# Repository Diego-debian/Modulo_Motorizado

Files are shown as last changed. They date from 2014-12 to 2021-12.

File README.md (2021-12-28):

Modulo Motorizado
=================

Bienvenido a este proyecto, el cual tiene como finalidad desarrollar un vehículo motorizado para poder ilustrar ciertas propiedades de las ondas electromagnéticas como los son: difracción, absorbción y atenuación; en este repositorio encontrara:
 1. Instalación de los paquetes de software necesarios.
 2. Los planos eléctricos del hardware.
 3. Programación del microcontrolador atmega 328
 4. Programa para la obtención de datos y graficador en tiempo real de dichos datos.
 5. Guías de elaboración de los laboratorios propuestos para ilustrar las propiedades de la radiación electromagnética. 
 6. Análisis de datos.
 7. Licencia de software.

Para comenzar la descarga del repositorio así como su instalación haga clic en la carpeta [0. Inicio] (/0. Instalación/)

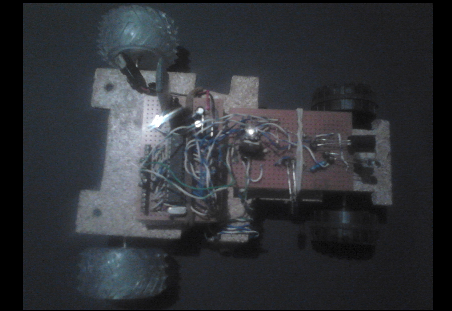
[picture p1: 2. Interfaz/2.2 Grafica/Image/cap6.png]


Objetivos
=========

# Generales 

 * Utilizar tecnologías libres para la realización de este proyecto.
 * Crear un modulo motorizado controlado vía bluetooth para ilustrar propiedades de la radiación infrarroja como lo son la difracción, la absorción y la atenuación. 

## Específicos 

 * Utilizar un Sistema operativo GNU-Linux como plataforma para el desarrollo del software que va a controlar el hardware del dispositivo.
 * Con el microcontrolador atmega328P-PU  realizar la parte de control del hardware.
 * Utilizar diodos led infrarrojos, tanto receptores como emisores, para la   construcción del sensor que llevara integrado nuestro proyecto.
 * Utilizar un motor a 9 voltios DC e integrarlo al vehículo, junto con un transistor TIP 122   para el control de la velocidad del motor.
 * Utilizar un modulo Bluetooth HC-06 para arduino, el cual permita la comunicación a distancia con el dispositivo, sin necesidad de un sistema físico cableado.
 * Utilizar un transistor LM-7805CV para construir un transformador de voltaje de 9 voltios a 5 voltios para poder alimentar el microcontrolador atmega328P-PU, y los demás dispositivos del proyecto.
 * Encontrar el patrón de difracción de los diodos emisores en infrarrojo para determinar la longitud de onda de los diodos.
 * Encontrar una constante en el patrón de absorción de diferentes materiales que nos permita clasificarlos por su capacidad de absorber radiación infrarroja.
 * Encontrar una constante en el patrón de atenuación la cual nos tiene que llevar a la conclusión de como se atenúa este tipo de radiación a través del espacio.

Metodología 
===========

 * Diseñar  una placa micro controladora que sea muy parecida a la placa arduino uno, con diodos emisores y receptores infrarrojos, resistencias, condensadores para la creación de los instrumentos de medición.
 * Construir un modulo motorizado “Vehículo motorizado”, con instrumentos para el análisis de radiación infrarroja, en donde reposara nuestra placa micro controladora y sus respectivos instrumentos de medición.
 * Utilizar un sistema operativo de software libre como lo es debian 7 Jessie o Linux mint 17, y con programas como  arduino, python, c++, octave, gnuplot, libreoffice, kile, fritzing y emacs para la creación del software.
 * Crear el software, adaptarlo y configurar bien al hardware para que no surjan errores significativos con las mediciones. 
 * Crear unas guías de laboratorio la cual sea de fácil comprensión tanto a estudiantes como profesionales que estén relacionados con estos temas.

Referencia Bibliográfica 
========================

 * Notas del curso, python para el computo científico, curso de actualización académica de la DGAPA-UNAM, Facultad de ciencias, Dr. David P. Sanders, 5 de agosto de 2013. 
 * Manual básico de uso de minicom http://www.slideshare.net/Metaconta/manual-bsico- minicom-presentation .
 * Para la placa arduino, se toma de referencia http://www.proyectosarduino.com/ 
 * Para la programación en la tarjeta micro controladora arduino se utilizara la siguiente referencia http://www.arduino.cc/es/ 
 * Para la programación en c++ y gcc, GNU/Linux, Programación de sistemas, Pablo Garaizar Sagarminaga, Facultad de Ingeniería -ESIDE, Universidad de Deusto, Bilbao. 
 * Fundamentos de circuitos eléctricos, tercera edición, editorial Mc Graw Hill, Charles K. Alexander and Matthew N. O. Sadiku. 
Manual del proyecto octave http://www.gnu.org/software/octave/doc/interpreter/ 
 * Pagina oficial del proyecto gnuplot http://www.gnuplot.info/ 
 * Pagina oficial del proyecto Libreoffice http://www.libreoffice.org/ 
 * Edición de textos científicos Latex, Walter Mora, Alexander Borbon
 * Escuela de matemática,Instituto Tecnológico de Costa Rica; Revista digital matemática, educación e Internet www.tec-digital.itcr.ac.cr/revistamatematica/ 
 * Manual del usuario emacs http://www.nongnu.org/emacs-man-es/ 
 * Pagina oficial del Sistema Operativo debian https://www.debian.org/index.es.html 
 * Pagina oficial del proyecto fritzing http://fritzing.org/home/ 
 * Física Macarenha Herrera Aguayo, Edición especial para el ministerio de educación Chileno, editorial Santillana. 
 * Berkeley Physics Course Vol 3 Ondas (Crawford), editorial Reverte 
 * Para el integrado microcontrolador atmega328 se utilizara esta pagina  http://www.futurlec.com/Atmel/ATMEGA328P-PU.shtml
 * Para el uso del TIP 122 se toma de referencia esta pagina http://pdf.datasheetcatalog.com/datasheet/fairchild/TIP122.pdf
 * Para el modulo Bluetooth HC-06 arduino se toma esta referencia http://42bots.com/tutorials/hc-06-bluetooth-module-datasheet-and-configuration-with-arduino/
 * Con el transistor LM7805CV se toma de referencia http://www.fairchildsemi.com/ds/LM/LM7805.pdf
 * Pagina oficial de Scilab http://www.scilab.org/
 * Pagina oficial de los productos  Phywe http://www.phywe.com/448/Product-Catalogue.htm

Mesa de Miembros del Proyecto
=============================

 1. Diego Alberto Parra Garzón <diegoestudianteud1@gmail.com> Desarrollador de Contenidos

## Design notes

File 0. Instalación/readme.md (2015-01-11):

Instalación 
===========

Para el correcto funcionamiento del programa es necesario instalar los siguientes programas:
 0. git 
 1. bluez* 
 2. gcc
 3. g++
 4. emacs
 5. gnuplot gnuplot-qt
 6. evince 
 7. octave
 8. python-matplotlib 
 9. python-numpy
 10. python-tk 
 11. python-gnuplot
 12. python-serial
 13. python-visual*
 14. libgtkglextmm*
 15. kile
 16. arduino 
 17. fritzing 
 18. eog
 19. arduino

Si desea o es usuario de un S.O. no mantenido por el script para su auto instalación o si solo desea instalar por su propia cuenta los programas por favor instalelos manualmente y pase a la etapa de clonar el sitio.

lo primero sera instalar git en su S.O. dependiendo su S.O. el comando puede variar en mi caso uso debian y por lo general se instala de la siguiente manera.
    
Ingresar como usuario root

    $ su  

Introducir el Password, atención por que cuando escribimos el pass no se escribe en la terinal y esto es debido a razones de seguridad, pero claro que si se esta escribiendo. Luego de logeados escribimos:

    $ apt-get install git 

Luego de instalado debera escribir en una terminal el siguiente comando, esta vez no como superusuario sino como usuario normal para esto escribimos exit, luego oprimimos enter y luego escribimos lo siguiente.

    $ git clone https://github.com/Diego-debian/Modulo_Motorizado.git

Despues de clonar el sitio nos dirijimos desde la terminal hasta donde descargamos el modulo git e ingresamos a la carpeta "Modulo_Motorizado/tree/master/0. Instalación/0.1 programas requeridos "

por favor ingrese a la carpeta antes mensionada y siga las instrucciones.

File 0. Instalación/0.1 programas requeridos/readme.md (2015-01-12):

# INSTALACION AUTOMATIZADA

Se encuentra en la parte de la instalación, en esta parte se procederá a instalar los paquetes necesarios para que el programa funcione, pues estos son requisitos fundamentales para el óptimo funcionamiento de todo el software.

 * Lo primero sera abrir una terminal y logearnos como usuario root.
 * Luego en la consola buscamos la ruta a nuestra a nuestro archivo de instalación en python la cual es "Modulo_Motorizado/tree/master/0. Instalación/0.1 programas requeridos". 
 * Encontramos un archivo llamado install.py, lo que debemos hacer es escribir en la terminal el siguiente comando.

     $ python install.py

 * El programa se ejecutara automaticamente, tendremos que esperar unos segundos mientras se carga.
 * Nos aparecera una ventana como la siguiente: 

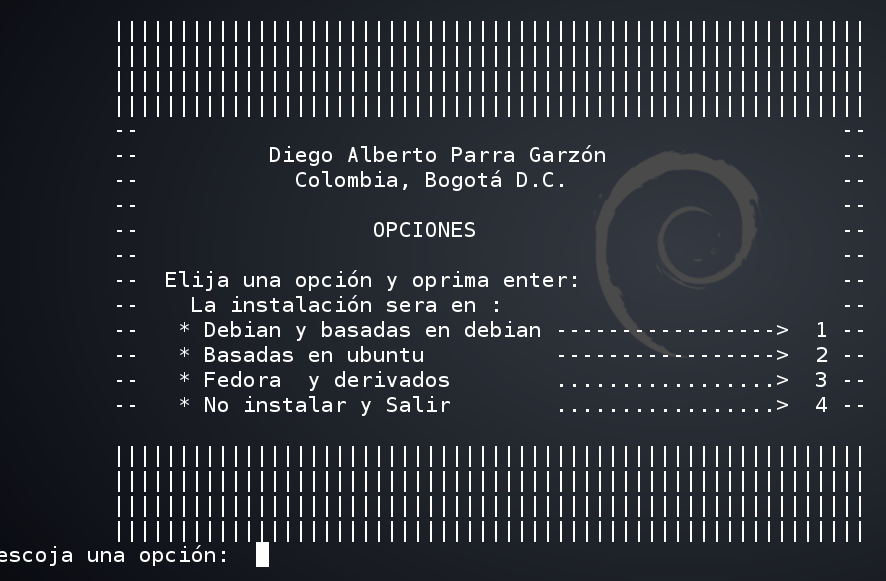
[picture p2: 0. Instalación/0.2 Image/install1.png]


 * Escogemos el S.O. que estamos usando, como ya dije de no aparecer el S.O., no hay ningún problema solo debemos instalar los paquetes antes mensionados manualmente y luego clonar el repositorio,
 * De aca en adelante le daremos "Si" a todo, y al finalizar nos aparecera la ventana de la IDE de arduino. 

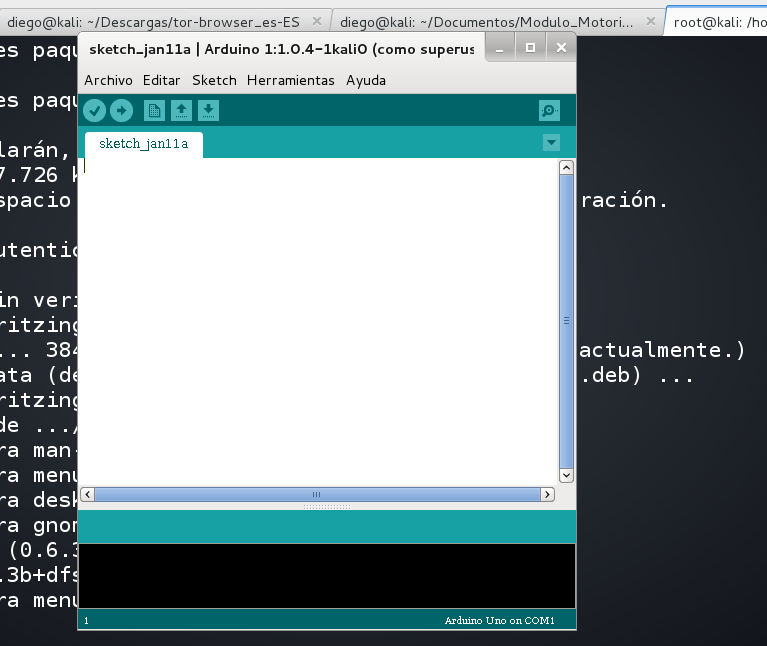
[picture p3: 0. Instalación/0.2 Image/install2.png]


 * Si se ha abierto esta ventana vamos por buen camino, ahora cerramos la ventana y el programa nos preguntara si queremos reiniciar el pc; a lo que responderemos que si.

Listo a disfrutar

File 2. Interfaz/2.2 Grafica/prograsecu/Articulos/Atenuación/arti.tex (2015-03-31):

\documentclass[12]{article}
\usepackage[spanish,english]{babel}
%\usepackage[spanish]{babel}
\usepackage[utf8]{inputenc}
\usepackage{graphicx}
\usepackage{epsfig}
\usepackage{multicol,caption}
\usepackage{amsthm} % Theorem Formatting
\usepackage{amssymb}    % Math symbols such as \mathbb
\usepackage{color}
\usepackage{hyperref}
\usepackage[none]{hyphenat}
%\renewcommand{\tablename}{Tabla}
%\def\tablename{Cuadro}% por \def\tablename{Tabla}% 
\newenvironment{Figure}
{\par\medskip\noindent\minipage{\linewidth}}
{\endminipage\par\medskip}
\addto\captionsspanish{%
\def\tablename{Tabla}%
}
\topmargin  = 10pt
\oddsidemargin  = -0.5in
%\headheight = 12pt
%\headsep    = 15pt
%\footskip   = 15pt
\textheight = 21.5 cm
\textwidth  = 18.5cm
\tolerance=10000
\title{\bf{Ilustración de la propiedad de atenuación en ondas electromagnéticas en el espectro infrarrojo, utilizando tecnologías libres y de bajo costo}}
\author{Diego Alberto Parra Garzón \footnote{diegoestudianteud1@gmail.com} \\ Universidad Distrital, Calle 3 No 26A-40 Bogotá-Colombia \\    Proyecto Curricular de Licenciatura en Física }
\date{\today}
\begin{document}
%\def\tablename{Cuadro}% por \def \tablename{Tabla}% 
\renewcommand{\tablename}{Tabla}
\maketitle
\vspace{-0.8cm}
\begin{abstract}
This article presents a new way of illustrating the attenuation property with electromagnetic waves; as the wavelengths in the infrared are also part of the electromagnetic spectrum and everyday use we give to this radiation is very wide, so it is essential to place this resource for both students and professionals, for the experimental part is combined with the theoretical giving a feedback issue. Data were obtained from a motor module equipped with an infrared sensor receiver and an infrared LED emitter, which are controlled by a atmega microcontroller 328-Pu and this is linked via Bluetooth to a computer, this process is done by the computer with the help of free software like python, gnuplot, octave among other languages, it is worth noting that everything is done in a free operating system like linux mint or debian. Data analysis laboratory, which will have to shed the value of attenuation of electromagnetic waves and has to match what is in the scientific literature will.\\ \\
{\bf{Keywords:}} Maxwell's laws, electromagnetic attenuation data nonlinear regression.
\end{abstract}
\selectlanguage{spanish}
\begin{abstract}
El presente articulo presenta una nueva forma de ilustrar la propiedad de atenuación que tienen las ondas electromagnéticas; como las longitudes de onda en el  infrarrojo también hacen parte del espectro electromagnético y el uso diario que le damos a esta radiación es muy amplio, por ello es indispensable colocar este recurso tanto para estudiantes como profesionales, pues se combina la parte experimental con lo teórico dando una retroalimentación del tema en cuestión. Se obtendrán los datos a partir de un modulo motorizado equipado con un sensor infrarrojo receptor y un led infrarrojo emisor, los cuales son controlados por un microcontrolador atmega 328-Pu y este va enlazado vía bluetooth a un ordenador, todo este proceso lo realiza el ordenador con la ayuda de software libre como python, gnuplot, octave entre otros lenguajes, cabe resaltar que todo se realiza en un sistema operativo libre como lo es linux mint o debian. Se hará el análisis de datos del laboratorio, el cual tendrá que arrojar el valor de atenuación de las ondas electromagnéticas y tiene que coincidir con el que se encuentra en la literatura científica.\\ \\
{\bf{Descriptores:}} Leyes de Maxwell, atenuación electromagnética, regresión no lineal de datos.
\end{abstract}
\begin{multicols}{2}
\section{Introducción}
El arreglo experimental esta esquematizado en la Fig. 1 y constaba de un horno con un pequeño orificio de salida para calentar el gas, luego de la salida un colimador y un selector de velocidades, y finalmente, un detector de partículas.
\end{multicols}
\end{document}

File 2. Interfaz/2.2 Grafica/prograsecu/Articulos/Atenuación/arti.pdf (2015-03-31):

# Ilustraci´on de la propiedad de atenuaci´on en ondas electromagn´eticas en el espectro infrarrojo, utilizando tecnolog´ıas libres y de bajo costo

## Diego Alberto Parra Garz´on ∗ Universidad Distrital, Calle 3 No 26A-40 Bogot´a-Colombia Proyecto Curricular de Licenciatura en F´ısica

## March 30, 2015

Abstract

This article presents a new way of illustrating the attenuation property with electromagnetic waves; as the wavelengths in the infrared are also part of the electromagnetic spectrum and everyday use we give to this radiation is very wide, so it is essential to place this resource for both students and professionals, for the experimental part is combined with the theoretical giving a feedback issue. Data were obtained from a motor module equipped with an infrared sensor receiver and an infrared LED emitter, which are controlled by a atmega microcontroller 328-Pu and this is linked via Bluetooth to a computer, this process is done by the computer with the help of free software like python, gnuplot, octave among other languages, it is worth noting that everything is done in a free operating system like linux mint or debian. Data analysis laboratory, which will have to shed the value of attenuation of electromagnetic waves and has to match what is in the scientific literature will.

Keywords: Maxwell’s laws, electromagnetic attenuation data nonlinear regression.

Abstract

El presente articulo presenta una nueva forma de ilustrar la propiedad de atenuaci´on que tienen las ondas electromagn´eticas; como las longitudes de onda en el infrarrojo tambi´en hacen parte del espectro electromagn´etico y el uso diario que le damos a esta radiaci´on es muy amplio, por ello es indispensable colocar este recurso tanto para estudiantes como profesionales, pues se combina la parte experimental con lo te´orico dando una retroalimentaci´on del tema en cuesti´on. Se obtendr´an los datos a partir de un modulo motorizado equipado con un sensor infrarrojo receptor y un led infrarrojo emisor, los cuales son controlados por un microcontrolador atmega 328-Pu y este va enlazado v´ıa bluetooth a un ordenador, todo este proceso lo realiza el ordenador con la ayuda de software libre como python, gnuplot, octave entre otros lenguajes, cabe resaltar que todo se realiza en un sistema operativo libre como lo es linux mint o debian. Se har´a el an´alisis de datos del laboratorio, el cual tendr´a que arrojar el valor de atenuaci´on de las ondas electromagn´eticas y tiene que coincidir con el que se encuentra en la literatura cient´ıfica.

Descriptores: Leyes de Maxwell, atenuaci´on electromagn´etica, regresi´on no lineal de datos.

## 1 Introducci´on

El arreglo experimental esta esquematizado en la Fig. 1 y constaba de un horno con un peque˜no orificio de salida para calentar el gas, luego de la salida un colimador y un selector de velocidades, y finalmente, un detector de part´ıculas.

∗diegoestudianteud1@gmail.com

1

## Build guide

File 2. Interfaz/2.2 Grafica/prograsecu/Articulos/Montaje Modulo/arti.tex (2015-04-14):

\documentclass[12]{article}
\usepackage[spanish,english]{babel}
%\usepackage[spanish]{babel}
\usepackage[utf8]{inputenc}
\usepackage{graphicx}
\usepackage{epsfig}
\usepackage{multirow}
\usepackage{multicol,caption}
\usepackage{amsthm} % Theorem Formatting
\usepackage{amssymb}    % Math symbols such as \mathbb
\usepackage{color}
\usepackage{hyperref}
\usepackage[none]{hyphenat}
%\renewcommand{\tablename}{Tabla}
%\def\tablename{Cuadro}% por \def\tablename{Tabla}% 
\newenvironment{Figure}
{\par\medskip\noindent\minipage{\linewidth}}
{\endminipage\par\medskip}
\addto\captionsspanish{%
\def\tablename{Tabla}%
}
\topmargin  = 10pt
\oddsidemargin  = -0.5in
%\headheight = 12pt
%\headsep    = 15pt
%\footskip   = 15pt
\textheight = 21.5 cm
\textwidth  = 18.5cm
\tolerance=10000
\title{\bf{Montaje de un modulo motorizado, con sensores infrarrojos, controlado con una tarjeta atmega 328P-PU y comunicación serial vía bluetooth en un ordenador con GNU-Linux.}}
\author{Diego Alberto Parra Garzón \footnote{diegoestudianteud1@gmail.com} \\ Universidad Distrital, Calle 3 No 26A-40 Bogotá-Colombia \\    Proyecto Curricular de Licenciatura en Física }
\date{\today}
\begin{document}
%\def\tablename{Cuadro}% por \def \tablename{Tabla}% 
\renewcommand{\tablename}{Tabla}
\maketitle
\vspace{-0.8cm}
\selectlanguage{english}

\begin{abstract}
It is necessary to visualize the extent that free technologies have today about the company, these technologies are the foundation of the economy of many countries, and why not say that it has reached an age where information and means to transmit they are available to anyone, such is the case we can take this technology and make it new tools to support the work of science teaching and learning in science, for this reason it has decided to take this whole world of free technologies, combine them and make it these new tools we need to continue this work of learning and teaching that never ends.\\ \\
illustrating the attenuation property with electromagnetic waves; as the wavelengths in the infrared are also part of the electromagnetic spectrum and everyday use we give to this radiation is very wide, so it is essential to place this resource for both students and professionals, for the experimental part is combined with the theoretical giving a feedback issue. Data were obtained from a motor module equipped with an infrared sensor receiver and an infrared LED emitter, which are controlled by a atmega microcontroller 328-Pu and this is linked via Bluetooth to a computer, this process is done by the computer with the help of free software like python, gnuplot, octave among other languages, it is worth noting that everything is done in a free operating system like linux mint or debian. Data analysis laboratory, which will have to shed the value of attenuation of electromagnetic waves and has to mat.\\ 
{\bf{Keywords:}} Motor module, infrared sensors, microcontroller module bluetooth, electromagnetic wave.

\selectlanguage{spanish}
\begin{center}
{\bf{Resumen}} 
\end{center}

Es necesario visualizar el alcance que las tecnologías libres tienen el día de hoy sobre la sociedad, estas tecnologías son las bases de las economías de muchos países, y porque no decirlo que se ha alcanzado una era en donde la información y los medios que la transmiten están al alcance de cualquier persona,  tal es el caso que podemos tomar esta tecnología y hacer de ella nuevos instrumentos que respalden la labor de la enseñanza científica y el aprendizaje en ciencias, por esta razón se ha decidido tomar todo este mundo de tecnologías libres, combinarlas y hacer de ella esos nuevos instrumentos que necesitamos para continuar con esta labor de aprendizaje y enseñanza que no termina nunca.\\\\
Este articulo espera ser acogido por estudiantes y profesionales que vean en este un modelo didáctico,  con materiales que consiguen fácilmente y con un gran poder de exactitud en las mediciones; en este  se ilustra un montaje experimental, de un modulo motorizado o en otras palabras un dispositivo móvil impulsado por un motor en este caso eléctrico; está equipado con un microcontrolador atmega 328P-PU, este se encargara de toda la parte de control de los demás elementos eléctricos, dispondrá de dos diodos led receptores en el infrarrojo   de GaAs, también consta de un diodo led emisor en el infrarrojo de GaAs, un modulo bluetooth hc-06 para arduino y una batería de 9 voltios junto con un regulador de 9V a 5V.  Todo esto con el fin de poder hacer mediciones de la intensidad de la radiación producida por estos diodos y calibrar el dispositivo para aplicaciones ilustrativas de las propiedades de las ondas electromagnéticas y su dualidad onda – partícula. \\
{\bf{Descriptores:}} Modulo motorizado, sensores infrarrojos, microcontrolador, modulo bluetooth, ondas electromagnéticas. 
\end{abstract}

\begin{multicols}{2}
\section{Introducción}
Al no poderse descartar la realidad de las tecnologías libres, su rápido crecimiento y el hecho de que sean muy sencillas de utilizar, ha sido el detonante para la realización de este proyecto; el cual pretende elaborar un sistema electrónico-mecánico que sea controlado vía bluetooth, sin necesidad de un sistema físico de cables; este debe tener la cualidad de ser lo más exacto posible en cuanto a la captura y manipulación de datos; sin dejar a un lado su bajo costo. \\\\ También tiene la pretensión de ser un modelo didáctico, que pueda ser utilizado en la enseñanza de la ciencia de una manera practica, llamativa, con la cual el estudiante pueda tener una sensación de que las ciencias son divertidas, sin dejar de lado su exactitud y su carácter de buscar el ¿por qué?,  los ¿cómo?, y la precisión al compararse la teoría con la parte experimental.

\section{Configuración experimental}

{\bf{2.1 Materiales para el montaje}} \\

Para la realización de este montaje se utilizaron los siguientes materiales:
\begin{enumerate}
\item[a.] Un ordenador con un sistema operativo GNU-Linux.
\item[b.] Microcontrolador atmega 328P-PU \cite{ARDUINO} para realizar la parte de control del hardware.
\item[c.] Dos diodos led infrarrojos\cite{INFRARED} receptores.
\item[d.] Un diodo led infrarrojo\cite{INFRARED} emisor.
\item[e.] Un motor a 9 voltios DC, junto con un transistor TIP 122\cite{TIP122}   para el control de la velocidad de giro del engranaje del motor.
\item[f.] Modulo Bluetooth HC-06 para arduino, el cual permita la comunicación a distancia con el dispositivo, sin necesidad de un sistema físico cableado.
\item[g.] Transistor LM-7805CV \cite{REGULADOR} para un transformador de voltaje de 9 voltios a 5 voltios el cual alimentara el microcontrolador atmega328P-PU, y los demás dispositivos del proyecto.
\item[h.] Un cristal de 16 MHz.
\item[i.] Tarjeta arduino \cite{ARDUINO} uno.
\item[j.] Tres resistencias de 220 ohms a 500 ohms.
\item[h.] Dos resistencia de 500 ohms.
\item[i.] Tres resistencias de 1 komhs.
\item[j.] Diodo rectificador de referencia 1N4001. \cite{DIODO}
\item[k.] Dos capacitores cerámicos de 12 picofaradios.
\item[l.] Dos capacitores de 10 microfaradios.
\item[m.] Sistema de engranajes de eje móvil, para realizar el movimiento del vehículo.
\item[n.] Cuatro llantas de carros de juguetes.
\item[ñ.] Una batería de 9 V.
\item[o.] Una tabla o un acrílico de 14x12x0.3 $cm^{3}$
\item[p.] Un interruptor pequeño.
\end{enumerate}

{\bf{2.2 Montaje experimental}}\\\\
{\bf{2.2.1 Circuito electrónico}}\\\\
A continuación se explica paso a paso como armar el circuito eléctrico, el montaje se realiza en fritzing\footnote{Enlace a la pagina oficial del proyecto fritzing http://www.fritzing.org/home/}. Se explicara parte por parte del circuito y luego todas deben unirse en una sola.\\\\
Cabe mencionar que los esquemas de las figuras de la 1 a la 8 fueron tomadas de la pagina principal del proyecto arduino\cite{ARDUINO}, y modificadas en fritzing\cite{FRITZING}  \\\\
Lo primero que se hará, sera preparar el microcontrolador para su primer uso, debido a que los microcontroladores atmega 328 P-PU no vienen listos para comenzar a programar; es necesario hacer un stand alone\footnote{Enlace a un bootloader https://arduinoelectronics.wordpress.com/2012/02/10/standalone-atmega-without-arduino-bootloader/} sobre el microcontrolador.\\\\

\begin{Figure}
\center
\begin{tabular}{|l|r|}
\hline
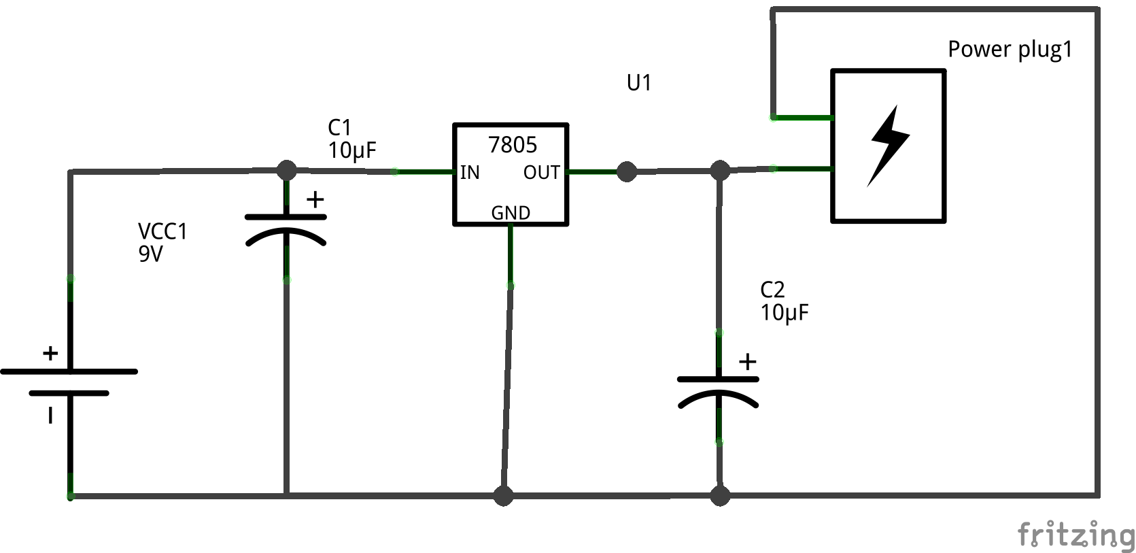
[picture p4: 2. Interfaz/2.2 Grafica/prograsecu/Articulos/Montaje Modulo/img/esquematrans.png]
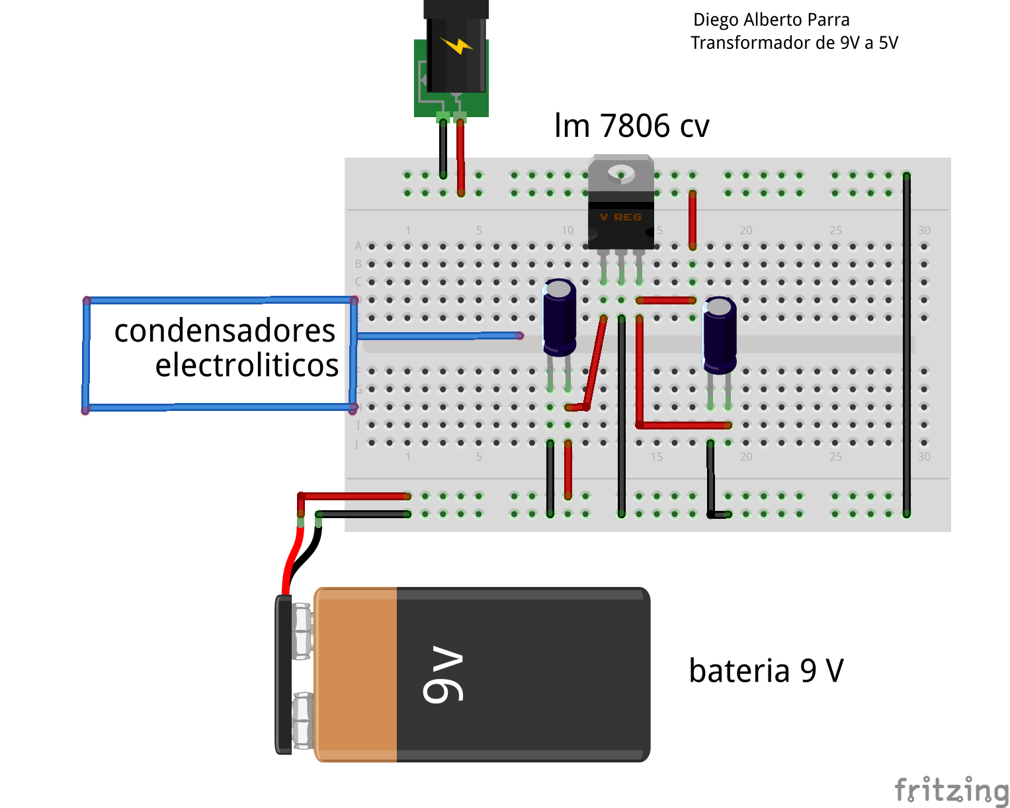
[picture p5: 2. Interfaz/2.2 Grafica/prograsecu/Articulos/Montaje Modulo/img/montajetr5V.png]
  &  \\ \hline
1.A. & 1.B \\ \hline
\end{tabular}
\captionof{figure}{En la figura 1.A. se observa el esquema eléctrico de un transformador \cite{REGULADOR} de 9V a 5V, utilizando un transistor lm 7805 cv. Los capacitores son electrolíticos de 10 microfaradios.  En la figura 1.B. se observa el montaje en protoboard del circuito regulador.}
\label{fig:g1}
\end{Figure}
\vspace{0.2cm}

Montamos un transformador de 9 voltios a 5 voltios, esto lo hacemos con dos capacitores electrolíticos de 10 microfaradios  y el transistor lm7805\cite{REGULADOR} cv. Ambos  capacitores deben ir en paralelo quedando su extremo negativo conectado a tierra y su extremo positivo uno a la entrada de 9 V y el otro a la salida de 5 V del transistor, el transistor lm consta de 3 pines uno de los cuales es la entrada de +9V, el pin de la mitad es tierra o GND y el pin extremo es la salida a 5V; tal como se muestra en la figura 1.A.; en la figura 1.B. se le coloco un enchufe de salida de poder.
El modulo bluetooth se debe conectar de la siguiente manera: el pin 2 de la tarjeta arduino es el Rx este va conectado al Tx del blueetooth, el pin 3 del microcontrolador es el Tx y va conectado al pin Rx del bluetooth, como se muestra en la figura 2.A y 2.B , conectamos el GND del bluetooth al pin 8  o 16 de nuestro microcontrolador , ahora conectamos el pin de Vcc del bluetooth al pin 7 o 14 del microcontrolador. \\\\
Necesitamos colocar un oscilador de 16 mHz el cual lo dejaremos siempre en el microcontrolador, esto  con el fin de ajustar los tres relojes internos que trae nuestro integrado atmega 328 P-Pu, para esto utilizamos el cristal de 16 mHz junto con los dos condensadores cerámicos de 12 picofaradios \footnote{Ver figura 2.A y 2.B.}, uno de los pines del cristal debe conectarse al pin 9 del microcontrolador y el otro extremo del cristal al pin 10, conectamos un capacitor a cada extremo del cristal y estos al pin 8 o 16 del microcontrolador de tal forma que los capacitores quedan en paralelo. \\\\
Colocamos un botón\footnote{Como se muestra en la figura 2.A y 2.B.} para reiniciar nuestro microcontrolador en caso de que lo necesitamos, esto lo hacemos colocando uno de los extremos del botón al pin 1 del microcontrolador que es el pin de reset, el otro extremo del botón lo conectamos a una resistencia de 1 Komhs y el extremo de la resistencia a tierra.\\\\

\begin{Figure}
\center
\begin{tabular}{|l|r|}
\hline
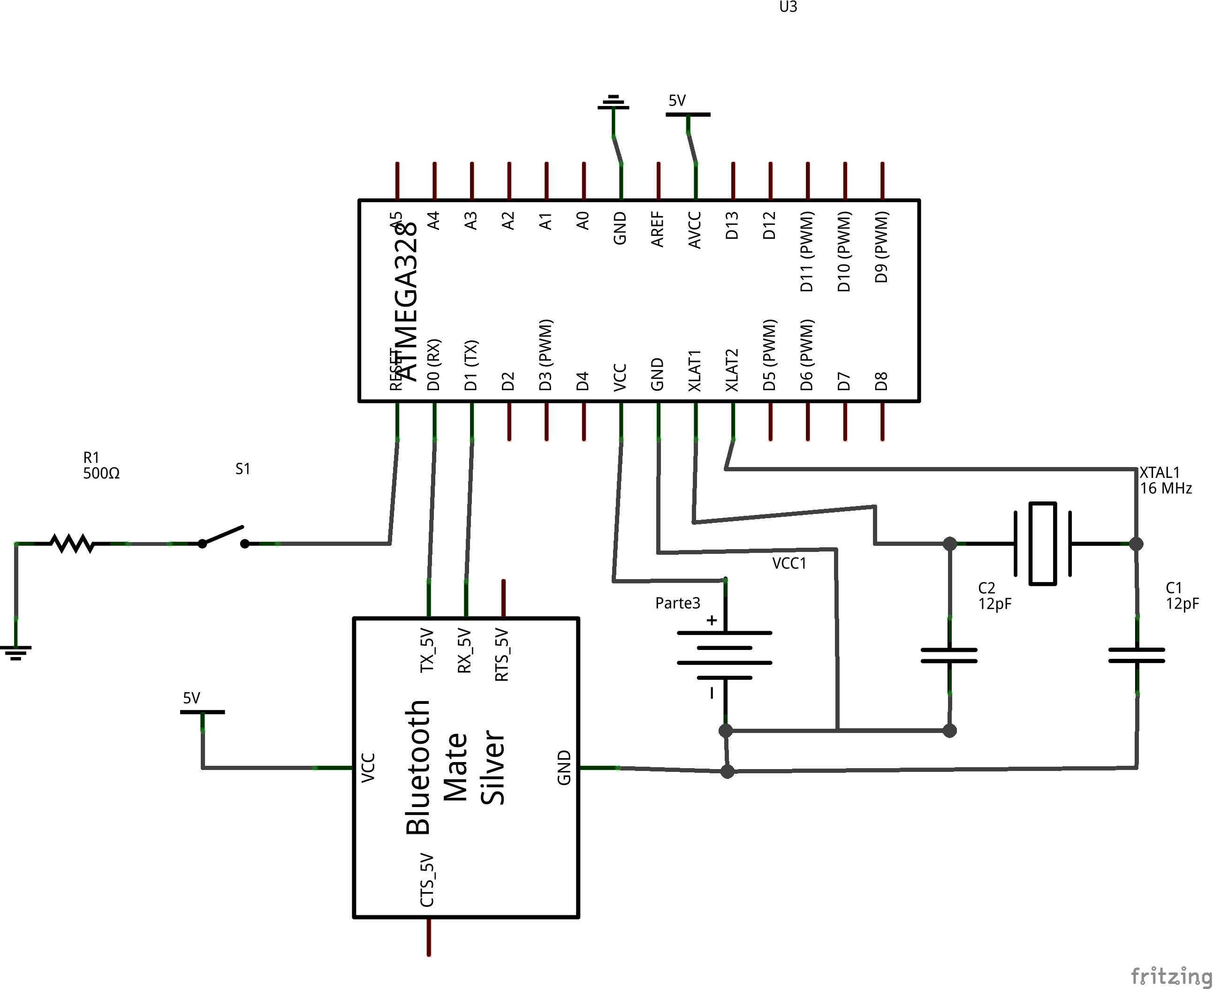
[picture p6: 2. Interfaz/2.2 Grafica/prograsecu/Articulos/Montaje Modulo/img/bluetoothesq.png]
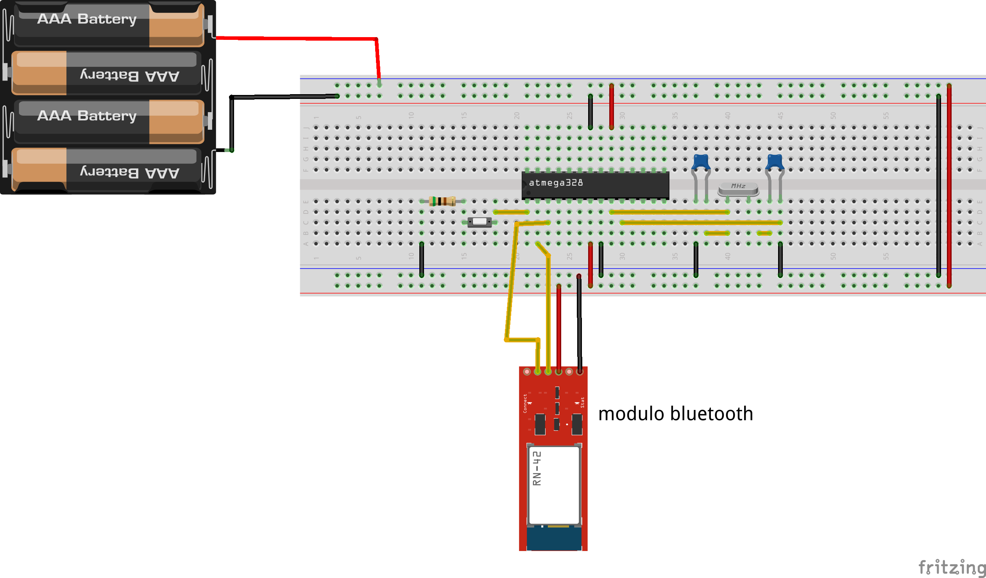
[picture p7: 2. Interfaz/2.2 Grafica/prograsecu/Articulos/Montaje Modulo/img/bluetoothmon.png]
 &  \\ \hline
2.A. & 2.B. \\ \hline
\end{tabular}
\captionof{figure}{En la figura 2.A se muestra el circuito eléctrico de un bluetooth conectado a un microcontrolador atmega 328 P-PU junto con un cristal, dos capacitores cerámicos, un botón de reset y una resistencia de 1 Komhs. En la figura 2.B esta  el montaje en protoboard, los cables negros son tierra, los cables rojos son voltaje, y los cables amarillos son conexiones.}
\label{fig:g2}
\end{Figure}
\vspace{0.2cm}

Las conexiones del motor son las siguientes, como vamos a utilizar un transistor tip\cite{TIP122} 122, los pines mostrados en la figura 2.B.  están de la siguiente manera: 

\begin{enumerate}
\item[*] El pin del lado izquierdo del transistor es la base.
\item[*] El pin del centro es el colector.
\item[*] El pin de la derecha es el emisor.
\end{enumerate}

Conectamos una resistencia de 1 $k \Omega $ al pin base del transistor y este a su vez al pin numero 5 del integrado atmega328P-PU\footnote{Como se aprecia en la figura 2.B.}, luego conectamos el pin del colector del tip122 a +5V, asegurándonos de colocar el diodo regulador entre el colector y uno de los extremos del motor; a continuación conectamos el pin emisor del transistor  junto con el otro extremo de la conexión del motor a tierra; ahora colocamos las conexiones del condensador cerámico entre las conexiones del motor.\footnote{Observar figuras 2.A. y 2.B.}

\begin{Figure}
\center
\begin{tabular}{|l|r|}
\hline
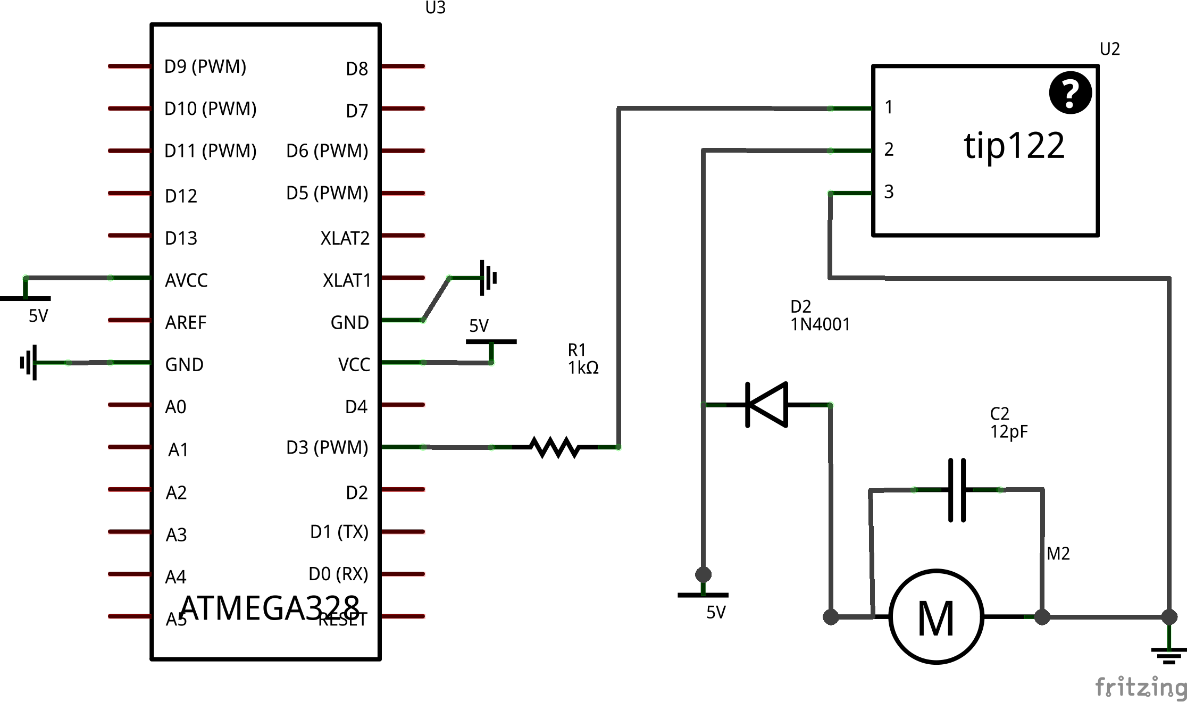
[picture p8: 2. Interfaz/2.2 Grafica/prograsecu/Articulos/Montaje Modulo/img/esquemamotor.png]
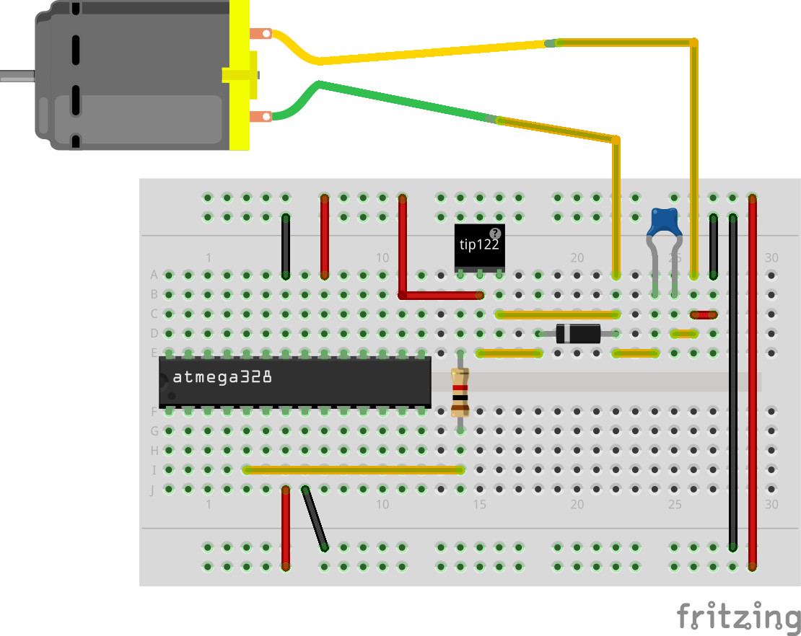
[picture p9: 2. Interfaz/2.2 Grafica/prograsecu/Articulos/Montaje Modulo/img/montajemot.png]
 &  \\ \hline
3.A. & 3.B. \\ \hline
\end{tabular}
\captionof{figure}{En la figura 3.A se muestra el circuito eléctrico del motor conectado a la tarjeta atmega 328 P-PU, junto con un tip 122 encargado de controlar la corriente que circula por el  motor consiguiendo de esta manera controlar la velocidad de este, también lleva un diodo regulador, un capacitor cerámico de  12 picofaradios y una resistencia de 1 Komhs. En la figura 3.B esta  el montaje en protoboard, los cables negros son tierra, los cables rojos son voltaje, y los cables naranjas son conexiones.}
\label{fig:g3}
\end{Figure}

Procedemos hacer las conexiones del sensor receptor lateral \footnote{Se aprecia en la figura 4.A. y en la figura 4.B.} el cual es un diodo led receptor de luz infrarroja \cite{INFRARED}, conectamos una resistencia de $1 k\Omega$ al ánodo del led y el otro extremo de la resistencia a tierra, luego conectamos el pin 28 \footnote{Este pin es la entrada analógica numero cero del microcontrolador atmega.} del microcontrolador en un punto intermedio entre la resistencia y el ánodo del diodo led, el cátodo del diodo lo conectamos a +5V.\\\\
Para las conexiones del sensor receptor frontal \footnote{Se aprecia en la figura 4.A. y en la figura 4.B., en la parte donde están los dos diodos led.} el cual es un diodo led receptor de luz infrarroja \cite{INFRARED}, conectamos una resistencia de $1 k\Omega$ al ánodo del led y el otro extremo de la resistencia a tierra, luego conectamos el pin 22 \footnote{Este pin es la entrada analógica numero cinco del microcontrolador atmega.} del microcontrolador en un punto intermedio entre la resistencia y el ánodo del diodo led, el cátodo del diodo lo conectamos a +5V.\\\\
Para la conexión de la fuente\footnote{Ver figura 4.B. y su esquema en la figura 4.A.} emisora de fotones infrarrojos o radiación infrarroja se utiliza un diodo led emisor en el infrarrojo, el cátodo del diodo lo conectamos a una resistencia de $350 \Omega$ a $500 \Omega$ y el otro extremo de la resistencia lo conectamos a tierra, el ánodo del diodo lo conectamos al pin 12\footnote{Salida D6 PWM.} del microcontrolador.

\begin{Figure}
\center
\begin{tabular}{|l|r|}
\hline
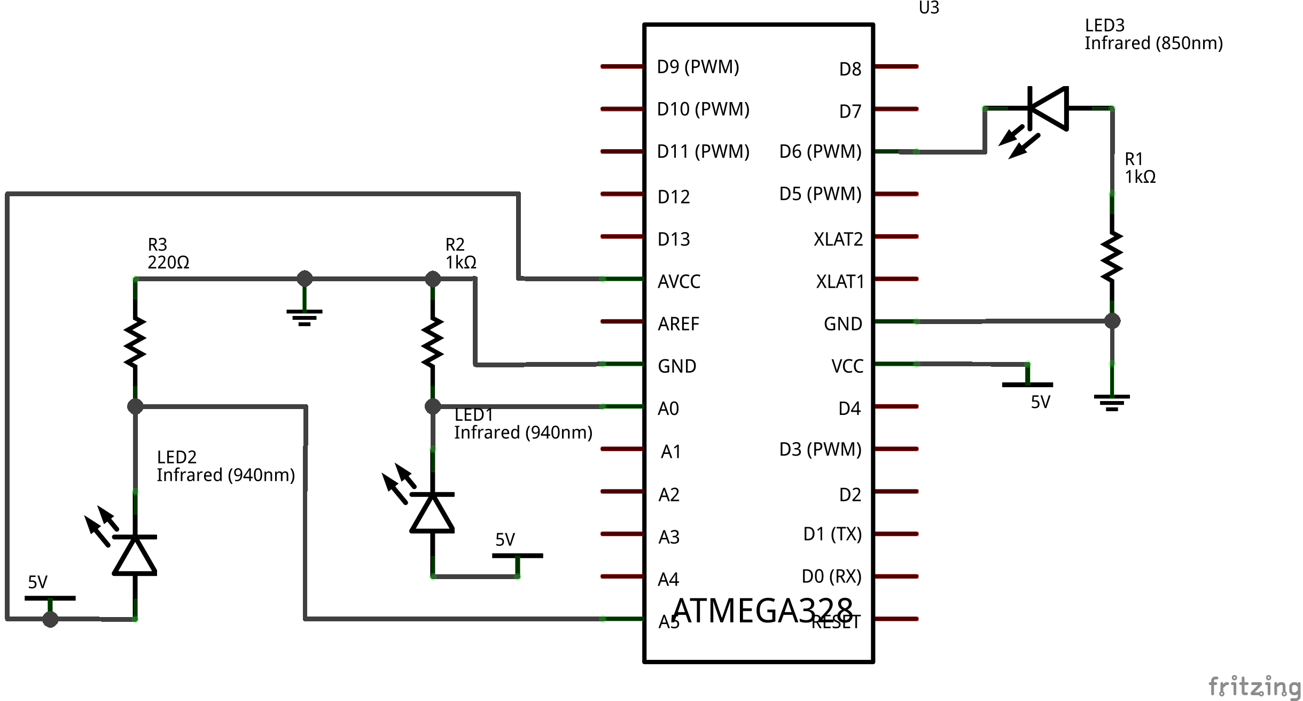
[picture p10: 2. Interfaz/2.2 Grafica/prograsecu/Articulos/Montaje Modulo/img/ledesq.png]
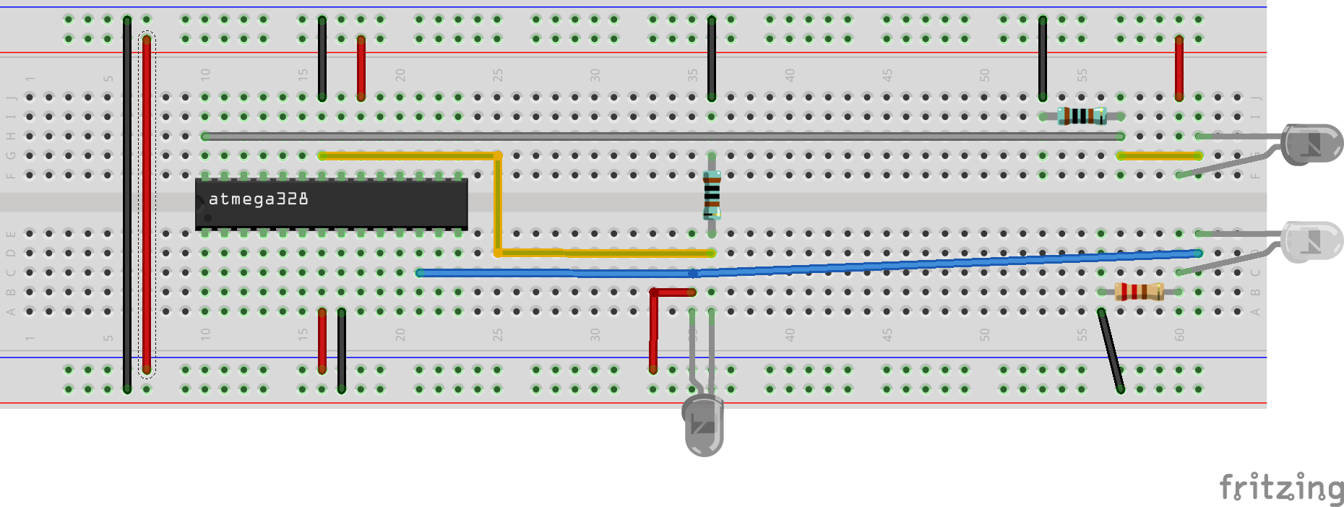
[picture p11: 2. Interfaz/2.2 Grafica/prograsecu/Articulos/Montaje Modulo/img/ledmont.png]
 &  \\ \hline
4.A. & 4.B. \\ \hline
\end{tabular}
\captionof{figure}{En la figura 4.A se observa las conexiones de los diodos tanto receptores como el emisor, conectamos al microcontrolador atmega328P-PU. En la figura 4.B esta  el montaje en protoboard, los cables negros son tierra, los cables rojos son voltaje, el cable azul es la conexión entre el ánodo del diodo led emisor infrarrojo frontal y el pin 6 del microcontrolador, el cable naranja es la conexión entre el pin 23 del microcontrolador y el punto de conexión entre el ánodo del  diodo receptor infrarrojo lateral con la resistencia, el cable gris  es la conexión entre el pin 28 del microcontrolador y el punto de conexión entre el ánodo del diodo receptor infrarrojo frontal con la resistencia.}
\label{fig:g4}
\end{Figure}

Las conexiones\footnote{Ver los esquemas de la figura 5.A. y 5.B.} del diodo rgb de ánodo común es la siguiente: conectamos el ánodo del diodo rgb a +5V, el pin rojo del diodo rgb lo conectamos a una resistencia de $500\Omega$ y el otro extremo de la resistencia conectado al pin 18 del microcontrolador, el pin verde del diodo rgb lo conectamos a una resistencia de $500\Omega$ y el otro extremo de la resistencia conectado al pin 16 del microcontrolador, el pin azul del diodo rgb lo conectamos a una resistencia de $500\Omega$ y el otro extremo de la resistencia conectado al pin 15 del microcontrolador.\\\\
Una vez terminadas las conexiones solo resta soldarlas en una baquela. Por ultimo pero no menos importante es conseguir icopor y hacer unas bases para que en ellas repose nuestro circuito de esta manera nos aseguramos en caso de cualquier incidente que las placas no se vayan a estropear ni que las conexiones vayan a quedar haciendo corto.
\begin{Figure}	
\center
\begin{tabular}{|l|r|}
\hline
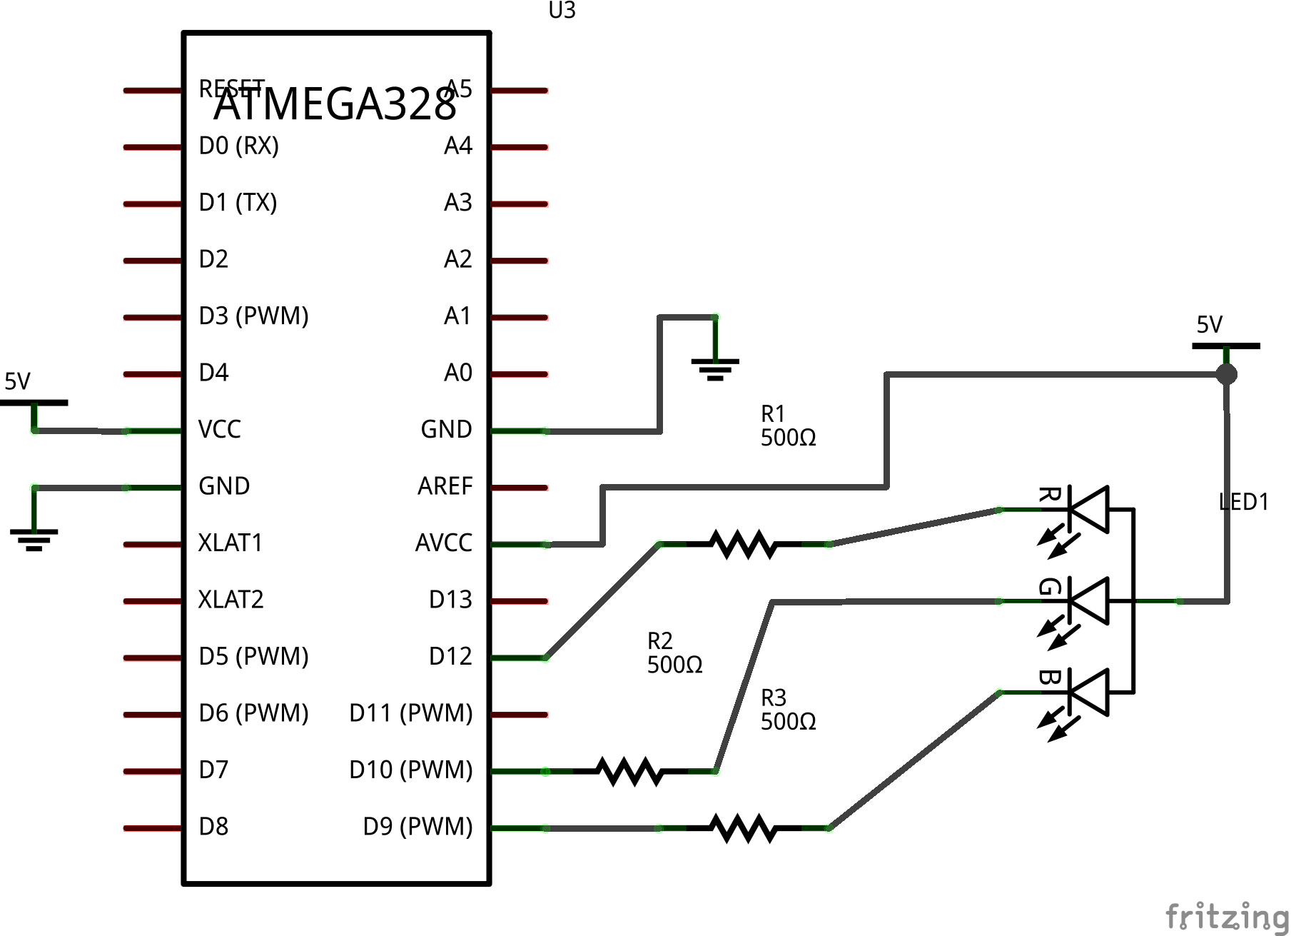
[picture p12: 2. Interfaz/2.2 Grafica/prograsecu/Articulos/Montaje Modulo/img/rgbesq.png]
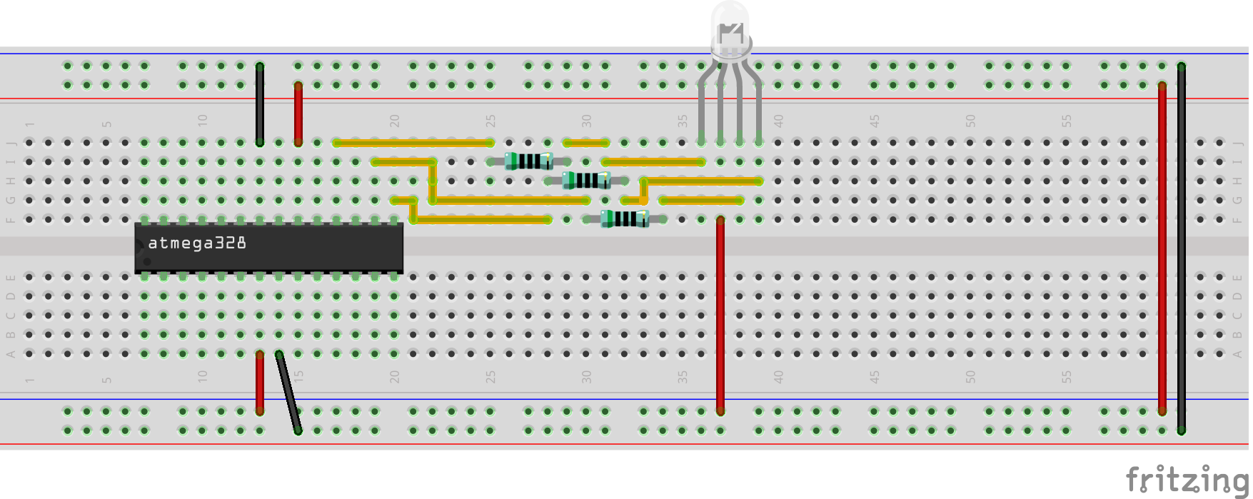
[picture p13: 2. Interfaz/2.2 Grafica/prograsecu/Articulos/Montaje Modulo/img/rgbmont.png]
 &  \\ \hline
5.A. & 5.B. \\ \hline
\end{tabular}
\captionof{figure}{En la figura 5.A. se muestra el circuito eléctrico del diodo rgb conectado al microcontrolador atmega 328 P-PU. En la figura 5.B esta  el esquema  del diodo rgb en protoboard.}
\label{fig:g5}
\end{Figure}
\vspace{0.6 cm}

Esa era la parte eléctrica ahora los esquemas eléctricos deben unirse para formar un solo circuito\footnote{Ver figura 6.A., y 6.B.}, antes de soldar el microcontrolador atmega 328P-PU es necesario cargar el archivo de control del hardware, cuyos pasos son los siguientes:
\begin{enumerate}
\item[a.] Instalar git \footnote{Enlace para instalar git  http://git-scm.com/download/linux }
\item[b.] Descargar el repositorio de este proyecto \footnote{En una terminal escribimos git  clone https://github.com/Diego-debian/Modulo\_Motorizado.git}.
\item[c.] Una vez descargado el repositorio hay que ir desde la terminal de linux a la carpeta donde se encuentra alojado el repositorio que acaba de descargar; si usted clono el repositorio en su carpeta home, solo coloque la siguiente linea en una terminal  sin la primera y ultima comilla “cd "Modulo\_Motorizado/0. Instalación/0.1 programas requeridos/"”.
\item[d.] Acceda como usuario root y a continuación escriba en la terminal la siguiente linea sin las comillas “python install.py”, se abrirá el programa de instalación del proyecto, ahora siga las instrucciones del programa.
\item[e.] Al terminar el programa le pedira si desea reiniciar el ordenador, escriba n y luego presione enter.
\item[f.] Escriba sin las comillas “exit” y oprima enter, luego escriba “arduino” y oprima enter, abrirá una ventana donde debe seleccionar la opción add. Luego de esto vera la IDE de arduino, ciérrela y reinicie el ordenador.
\item[g.] Desde nuestro navegador de archivos del sistema\footnote{Puede estar utilizando los siguientes en su distribución linux, nautilus, thunar o algún otro.}  entramos a la carpeta Modulo\_Motorizado/1. Inicio/ 1.2 programar arduino y sensores, allí encontraremos el archivo sensores2.ino, lo seleccionamos y oprimimos enter.
\item[h.] Conectamos la tarjeta arduino junto con el microcontrolador que vamos a dejar en el proyecto, en la IDE de arduino vamos a la opción herramientas,  tarjeta y seleccionamos arduino uno;  ahora nuevamente en herramientas, damos click en puerto serial y seleccionamos el puerto que nos aparece,  ahora oprimimos la tecla ctrl y la tecla “u” \footnote{Sin las comillas.} al mismo tiempo y esperamos mientras carga el sketch, una vez cargado retiramos el microcontrolador y lo colocamos en la parte del proyecto donde se le dispuso su sitio.   
\end{enumerate}

\begin{Figure}	
\center
\begin{tabular}{|l|r|}
\hline
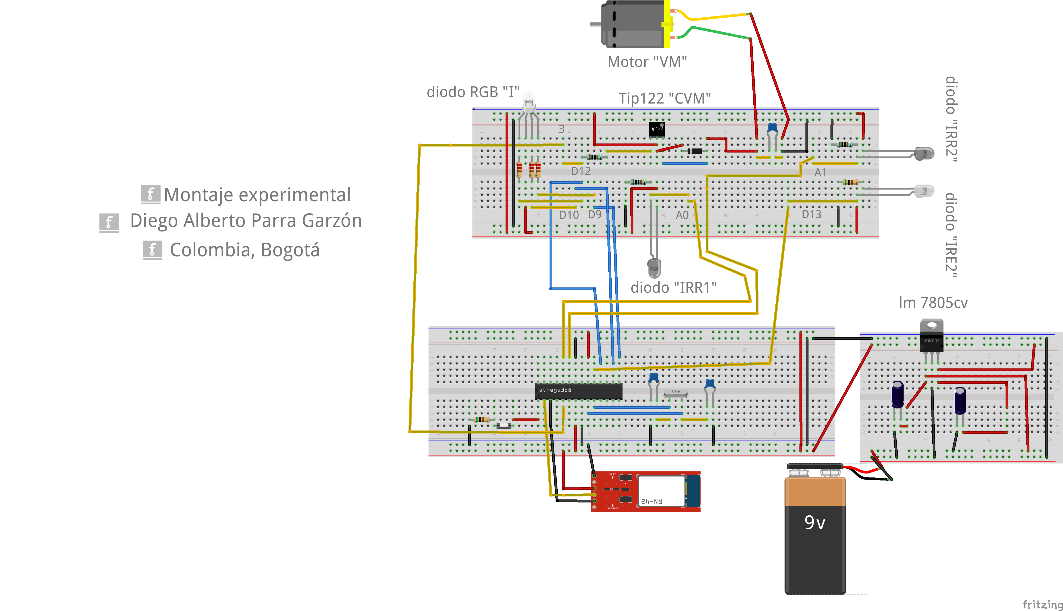
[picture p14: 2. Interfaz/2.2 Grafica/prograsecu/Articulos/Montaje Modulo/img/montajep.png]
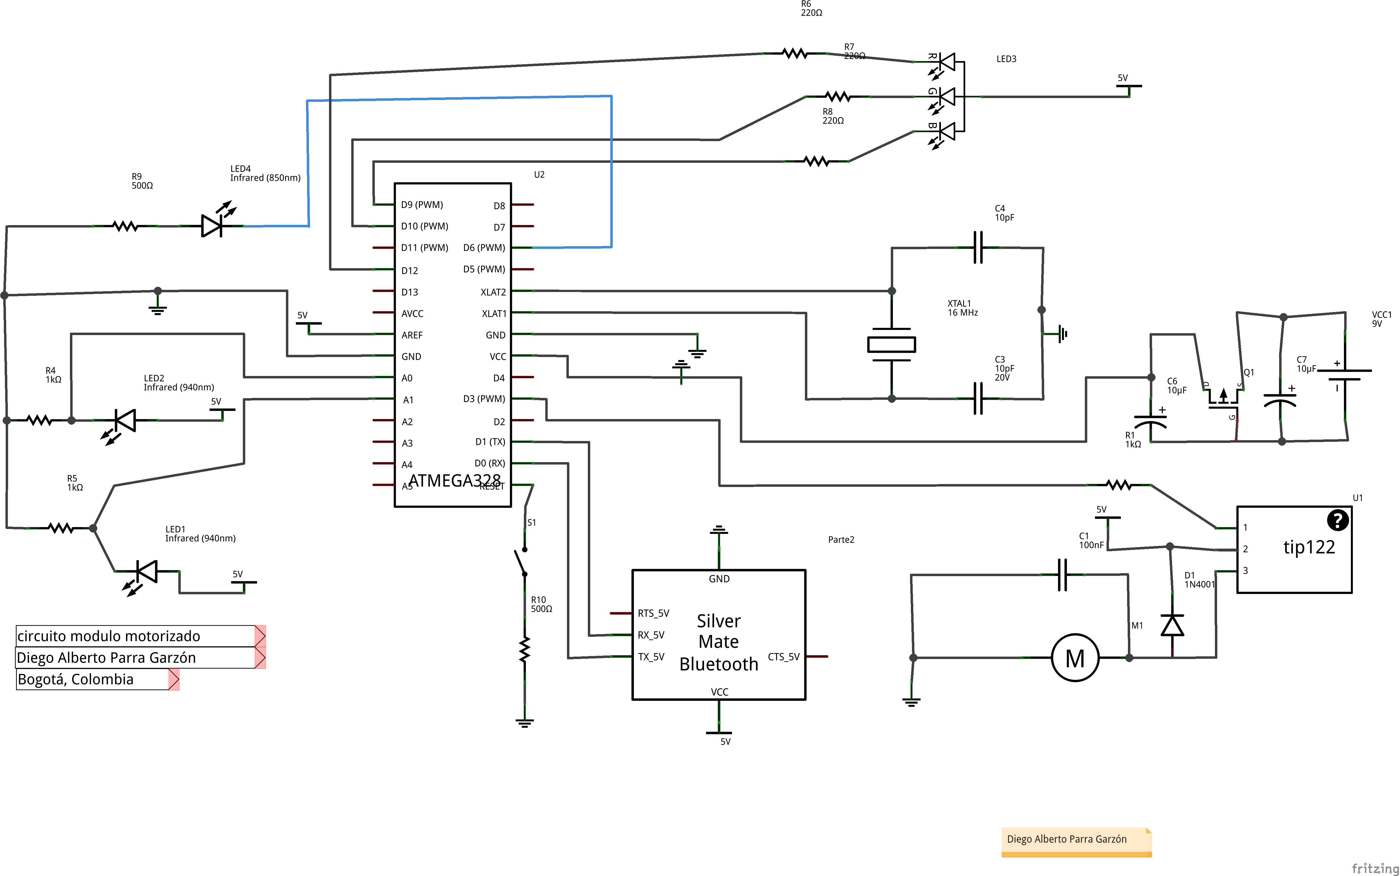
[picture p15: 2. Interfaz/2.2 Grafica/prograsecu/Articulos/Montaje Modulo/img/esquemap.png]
 &  \\ \hline
6.A. & 6.B. \\ \hline
\end{tabular}
\captionof{figure}{En la figura 6.A. se muestra el circuito eléctrico del proyecto. En la figura 5.B esta  el esquema  del proyecto.}
\label{fig:g6}
\end{Figure}
\vspace{0.6 cm}

{\bf{2.2.1 Montaje mecánico}}\\\\
Lo primero sera tomar la tabla de madera o acrílico y hacer un chasis  como el que aparece en la figura 7, para montar nuestro sistema de transmisión\footnote{Ver figura 8.B.}, el circuito eléctrico, y el sistema de rodamiento delantero\footnote{Ver figura 8.A. y 8.B.}.
\begin{Figure}	
\center
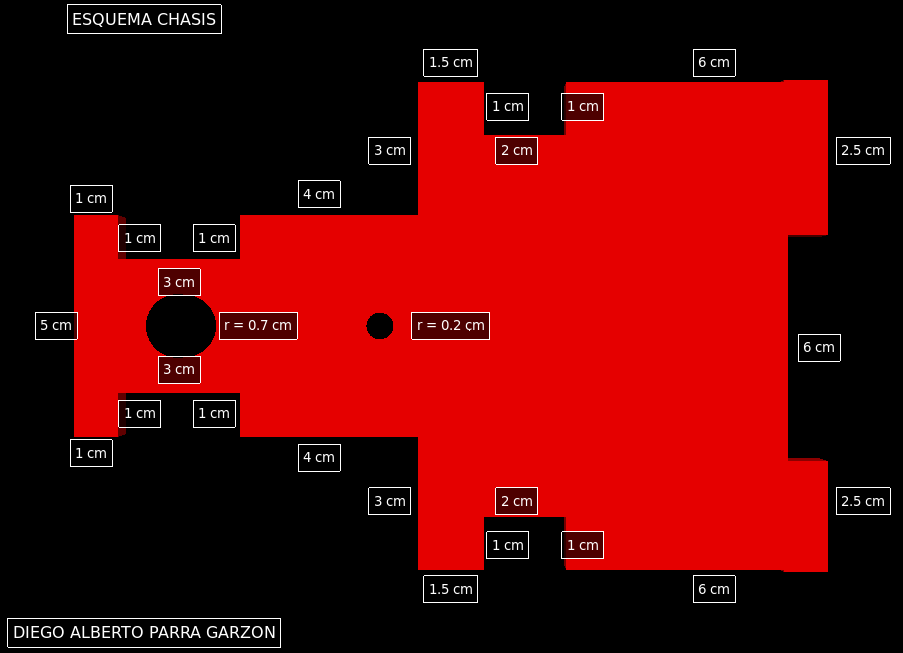
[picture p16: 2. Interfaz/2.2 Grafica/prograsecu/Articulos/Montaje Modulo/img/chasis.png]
 
\captionof{figure}{En esta figura se observan las dimensiones del chasis que va servir de base del circuito eléctrico y donde reposara el sistema de transmisión del proyecto. Esta figura fue modelada en python visual.}
\label{fig:g7}
\end{Figure}
\vspace{0.6 cm}
Ahora colocamos las llantas del vehículo para esto colocamos dos llantas de 1.5 cm de radio en el eje delantero y luego colocamos dos llantas de 2.5 cm de radio en los ejes traseros; esto con el fin de reducir la rapidez angular de las llantas, la cual se manifestara en una disminución significativa de la rapidez del vehículo.\\\\
Después de tener todo montado como se aprecia en la figura 9, hemos terminado toda la parte del montaje del modulo motorizado.\\\\

\begin{Figure}	
\center
\begin{tabular}{|l|r|}
\hline
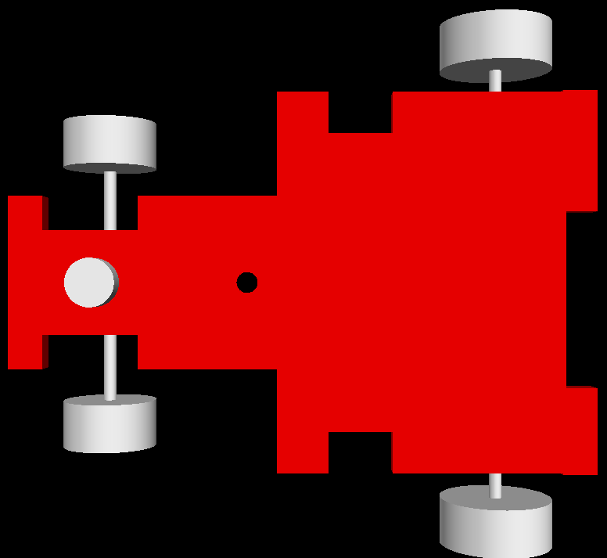
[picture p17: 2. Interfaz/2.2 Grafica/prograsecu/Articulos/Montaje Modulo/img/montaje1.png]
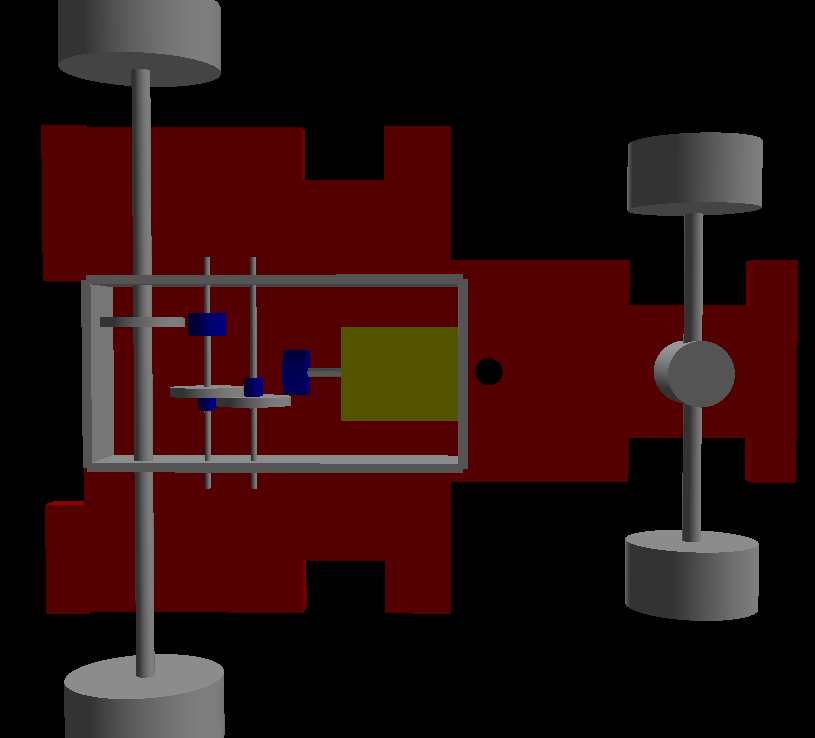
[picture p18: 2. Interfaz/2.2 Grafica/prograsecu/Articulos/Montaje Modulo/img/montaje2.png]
 &  \\ \hline
8.A. & 8.B. \\ \hline
\end{tabular}
\captionof{figure}{En la figura 8.A. se muestra la vista superior del montaje del vehículo motorizado, solo falta colocar la parte eléctrica. En la figura 8.B se muestra el montaje del vehículo motorizado con una vista inferior, junto al sistema de transmisión, y el rodamiento delantero. Las figuras fueron modeladas en python visual.}
\label{fig:g8}
\end{Figure}
\vspace{0.6 cm}

Este vehículo se encuentra en una etapa alpha, de esta manera hace falta montar toda la parte estética del vehículo, esto se deja a disposición de cada persona, pues lo realmente importante del vehículo es sus funciones, pero no hay que olvidar que la parte estética es y sera muy importante si este producto quisiera comercializarse.  \\\\

\begin{Figure}	
\center
 
\captionof{figure}{Este es el montaje final del vehiculo motorizado.}
\label{fig:g9}
\end{Figure}
\vspace{0.6 cm}

\section{Experiencia de laboratorio}

Una vez descargado nuestro repositorio del proyecto, y teniendo listo el montaje del mismo, es necesario hacer las respectivas pruebas de rapidez e intensidad de radiación del vehículo, para poder realizar estos análisis fue necesario crear una interfaz gráfica en python\cite{PYTHON} que fuera capaz de controlar el  vehículo, obtener datos de este y hacer sus respectivos análisis.\\\\
{\bf{3.1 Pruebas de rapidez}} \\\\
Lo primero que debemos hacer es desde una terminal dirigirnos hasta la carpeta donde hemos descargado nuestro repositorio, luego escribimos cd “Modulo\_Motorizado/2. Interfaz/2.2 Grafica”; ahora escribimos python Gverificar.py  y oprimimos enter, nos debe aparecer la interfaz gráfica de bienvenida, en la que encontraremos una imagen con nuestro vehículo, damos click en la imagen e inmediatamente se nos abrirá otra ventana en donde encontraremos las opciones que necesitamos, damos click en la opción que dice prueba 1, esto nos abrirá otra ventana en la que nos pide la ruta al dispositivo, para esto  escribimos en la terminal blueman-manager, damos al icono de la lupa y nos buscara los dispositivos bluetooth disponibles, apenas veamos nuestro modulo bluetooth, que por lo general siempre aparece como HC-06 o HC-05, damos click derecho sobre este, seleccionamos la opción de emparejar y escribimos la clave de paso, por default es 1234; ahora una vez emparejado procedemos hacer click derecho nuevamente sobre el dispositivo y damos click en la opción “dev B”, si todo sale bien nos dará vía libre al puerto serial y nos dirá la ruta al dispositivo; una vez tengamos el nombre de la ruta al dispositivo la escribimos en la ventana de nuestro programa y damos enter\footnote{Ver figura 10.}, a lo que nos aparecerá, múltiples opciones  para calibrar la rapidez a la que se mueve nuestro modulo. En la primera parte nos aparece las opciones de rapidez sin pausa, por lo que al dar click en cualquiera de estas opciones sin pausa el vehículo se moverá durante 5 segundos a lo que debemos medir la distancia que se desplazo el vehículo, esto lo debemos hacer con cada una de las opciones y de esta manera saber cual es la rapidez a la que se mueve nuestro vehículo. Acto seguido nos aparece las opciones de rapidez con pausa, en esta parte el vehículo se moverá pausadamente 20 veces, por lo que debemos medir la distancia final del vehículo y dividir esta distancia por el numero de veces que se movió, de esta manera conseguimos el desplazamiento en cada pausa. 

\begin{Figure}	
\center
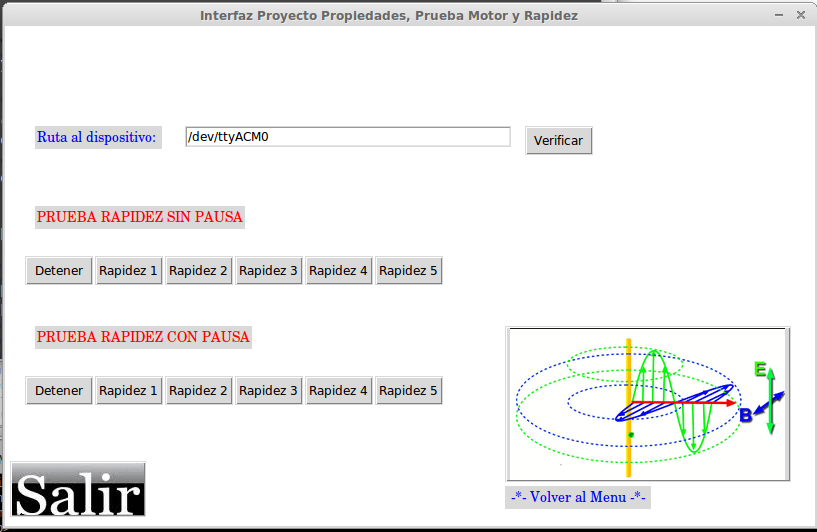
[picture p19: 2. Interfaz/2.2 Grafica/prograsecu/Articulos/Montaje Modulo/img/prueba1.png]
 
\captionof{figure}{Este es el programa para realizar las pruebas de rapidez con y sin pausa.}
\label{fig:g10}
\end{Figure}
\vspace{0.6 cm}

{\bf{3.2 Pruebas sensor lateral}}\\\\
Una vez terminada la prueba de rapidez en el vehículo, damos click en la imagen de una onda electromagnética, luego oprimimos en el botón que dice prueba 2, una vez allí volvemos a colocar la ruta a nuestro dispositivo, que es la misma que la prueba 1; damos click y nos aparecen dos pruebas una con rapidez sin pausa y otra de rapidez con pausa; el principio que utilizamos aquí es el de electro-recepción pasiva\cite{CIRCUITOS}, pues nuestro diodo receptor\cite{INFRARED} solo esta recibiendo la radiación y este a su vez se comporta como un  transductor\cite{CIRCUITOS}, pues convierte nuestra radiación electromagnética\footnote{Parte clásica.} o los fotones\footnote{Parte cuántica.}, en electricidad, que es interpretada  por nuestro microcontrolador como aumento en la corriente en uno de sus pines receptores análogos,  causando una diferencia de potencial\cite{CIRCUITOS}, con esta diferencia de potencial se trabajara para calibrar nuestro instrumento y poder hacer de el lo más confiable que se pueda en cuanto a sus mediciones refiere.\\\\

\begin{Figure}	
\center
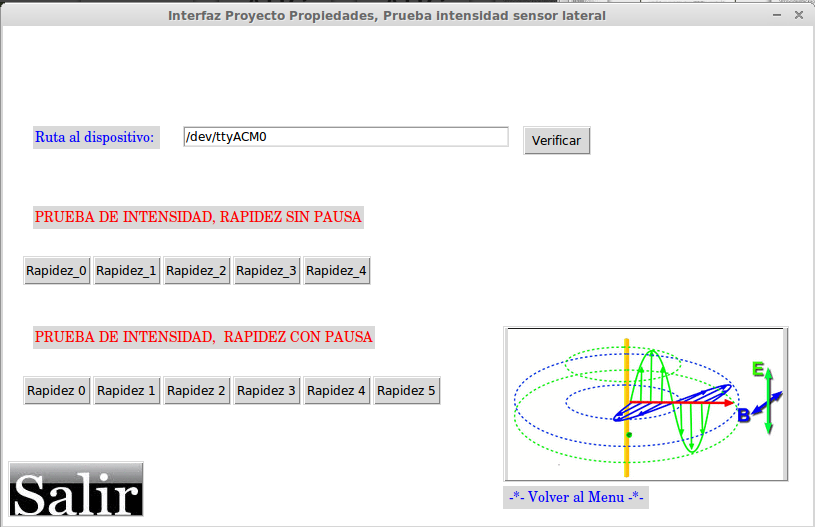
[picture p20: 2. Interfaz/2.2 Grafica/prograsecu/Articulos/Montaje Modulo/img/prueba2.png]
 
\captionof{figure}{Este es el programa para realizar las pruebas del sensor lateral.}
\label{fig:g11}
\end{Figure}
\vspace{0.6 cm}

Para realizar la prueba de rapidez sin pausa es necesario un ambiente\footnote{No debe estar presente la luz solar ni ninguna fuente que genere cantidades significativas de radiación infrarroja.} controlado,\footnote{Una temperatura ambiente inferior a los 18 $C^{0}$, las hojas de datos de estas piezas electrónicas indican que a temperaturas superiores la corriente no es lineal.} ahora lo primero sera medir la cantidad de datos que es capaz de procesar nuestro ordenador por segundo, para esto oprimimos el botón de rapidez 0 y cambiamos a la ventana de la terminal que esta ejecutando el programa, una vez allí el programa empezara hacer una medición del tiempo que tarda nuestro ordenador en procesar 200 datos\footnote{Para mayor información de esta parte, favor oprimir el botón de ayuda del programa.}, este resultado aparece en nuestra terminal\footnote{El programa va calibrado para trabajar en un ordenador toshiba satellite de 4 Gb de ram.}, mientras captura los datos los gráfica en tiempo real\footnote{Esta parte del código fue creada por mi al no tener un graficador en tiempo real para el puerto serial en GNU-Linux con python.};  una vez hecho esto cerramos la gráfica y cambiamos algunas partes del código\footnote{Ver la sección ayuda del proyecto.} para medir nuevamente  la distancia a la que se desplaza nuestro vehículo después de un tiempo prudencial y de esta manera obtener la rapidez a la que se desplaza nuestro modulo,  ahora es necesario volver a cambiar nuestro código\footnote{Ver sección ayuda del proyecto.}, esto con el fin de obtener unos buenos datos, por ultimo el programa nos mostrara la cantidad de ruido que interfiere en el experimento.  \\\\
Ahora hacemos lo mismo con la parte de rapidez con pausa\footnote{Ver sección ayuda del proyecto.}.\\

{\bf{3.3 Pruebas dispositivo frontal}}\\

Una vez terminada la prueba 2, damos click en la imagen de una onda electromagnética, luego oprimimos en el botón que dice prueba 3, una vez allí volvemos a colocar la ruta a nuestro dispositivo, que es la misma que la prueba 2; damos click y nos aparecen dos pruebas una con rapidez sin pausa y otra de rapidez con pausa; el principio que utilizamos aquí es el de electro-recepción activa\cite{CIRCUITOS}, este consiste en enviar una señal, y luego por las propiedades\cite{BERKELEY} de reflexión\cite{HECHT}, absorción\cite{HECHT}, atenuación\cite{HECHT}, esta llega a nuestro diodo receptor\cite{INFRARED}, osea que es necesario enviar energía, para que esta vaya y vuelva rebotando de los obstáculos a nuestro sensor y este a su vez se comporta como un  transductor\cite{CIRCUITOS}, pues convierte nuestra radiación electromagnética\footnote{Parte clásica.} o los fotones\footnote{Parte cuántica.}, en electricidad, que es interpretada  por nuestro microcontrolador como aumento en la corriente en uno de sus pines receptores análogos,  causando una diferencia de potencial\cite{CIRCUITOS}, con esta diferencia de potencial se trabajara para calibrar nuestro instrumento y poder hacer de el lo más confiable que se pueda en cuanto a sus mediciones refiere.

\begin{Figure}	
\center
 
\captionof{figure}{Este es el programa para realizar las pruebas del sensor lateral.}
\label{fig:g11}
\end{Figure}
\vspace{0.4 cm}

Para realizar la prueba de rapidez sin pausa es necesario un ambiente\footnote{No debe estar presente la luz solar ni ninguna fuente que genere cantidades significativas de radiación infrarroja.} controlado,\footnote{Una temperatura ambiente inferior a los 18 $C^{0}$, las hojas de datos de estas piezas electrónicas indican que a temperaturas superiores la corriente no es lineal.} ahora lo primero sera medir la cantidad de datos que es capaz de procesar nuestro ordenador por segundo, para esto oprimimos el botón de rapidez 0 y cambiamos a la ventana de la terminal que esta ejecutando el programa, una vez allí el programa empezara hacer una medición del tiempo que tarda nuestro ordenador en procesar 200 datos\footnote{Para mayor información de esta parte, favor oprimir el botón de ayuda del programa.}, este resultado aparece en nuestra terminal\footnote{El programa va calibrado para trabajar en un ordenador toshiba satellite de 4 Gb de ram.}, mientras captura los datos los gráfica en tiempo real\footnote{Esta parte del código fue creada por mi al no tener un graficador en tiempo real para el puerto serial en GNU-Linux con python.};  una vez hecho esto cerramos la gráfica y cambiamos algunas partes del código\footnote{Ver la sección ayuda del proyecto.} para medir nuevamente  la distancia a la que se desplaza nuestro vehículo después de un tiempo prudencial y de esta manera obtener la rapidez a la que se desplaza nuestro modulo,  ahora es necesario volver a cambiar nuestro código\footnote{Ver sección ayuda del proyecto.}, esto con el fin de obtener unos buenos datos, por ultimo el programa nos mostrara la cantidad de ruido que interfiere en el experimento.  \\\\
Ahora hacemos lo mismo con la parte de rapidez con pausa\footnote{Ver sección ayuda del proyecto.}.

\section{Analisis de resultados}
{\bf{4.1 Análisis de la Prueba 1}}\\\\
Después de cerca de 100 mediciones en cada una de las opciones de esa sección del proyecto se llegan a las siguientes conclusiones: \\\\
{\bf{4.1.1 Rapidez sin pausa}}\\

En la tabla 1 se puede apreciar los resultados de la prueba de rapidez sin pausa en cada opción del programa, se trabaja con un corriente menor que la salida del pin analógico que es de 35 mA.\\\\
El error en la medida de los datos de rapidez es la misma que nos ofrece nuestro instrumento de medición que en este caso es un metro cuyo error es $\frac{+}{-} 1 mm$, el error en la medida de la corriente es de $\frac{+}{-} 1 mA$.\\

\begin{tabular}{|l|c|c|} 
\hline
\bf{Opción} &  \bf{Rapidez $(\frac{m}{s})$} & \bf{Corriente (mA)}\\
\hline
Rapidez 1 & 0.103 & 20 \\
\hline
Rapidez 2 & 0.130 & 23 \\
\hline
Rapidez 3 & 0.138 & 24 \\
\hline 
Rapidez 4 & 0.154 & 25 \\
\hline
\end{tabular}
\\
\textbf{Tabla 1.} Datos obtenidos de la Prueba 1, rapidez sin pausa, la corrientes es la que circula por el motor con cada opción. \\

{\bf{4.1.2 Rapidez con pausa}} \\
En la tabla 2 se puede apreciar los resultados de la prueba de rapidez con pausa en cada opción del programa, se trabaja con un corriente menor que la salida del pin analógico que es de 35 mA.\\\\
El error en la medida de los datos de rapidez es la misma que nos ofrece nuestro instrumento de medición que en este caso es un metro cuyo error es $\frac{+}{-} 1 mm$, no se calcula la corriente pues varia demasiado rapido para ser medida.\\

\begin{tabular}{|l|c|c|} 
\hline
\bf{Opción} & Distancia final (cm) & Avance (cm)\\
\hline
Rapidez 1 & 9 &0.45 \\
\hline
Rapidez 2 & 8 &0.4 \\
\hline
Rapidez 3 & 6.5 &0.325 \\
\hline 
Rapidez 4 & 6 & 0.3 \\
\hline
\end{tabular}
\\
\textbf{Tabla 2.} Datos obtenidos de la Prueba 1, rapidez con pausa, la distancia final es la distancia después de 20 repeticiones, y la distancia de avance es la distancia final dividida 20 repeticiones. \\

{\bf{4.2 Sensor lateral}} \\\\
{\bf{4.2.1 Rapidez sin pausa}}\\\\
En la tabla 1 se puede apreciar los resultados de la prueba de rapidez sin pausa en cada opción del programa, se trabaja con un corriente menor que la salida del pin analógico que es de 35 mA.\\\\
El error en la medida de los datos de rapidez es la misma que nos ofrece nuestro instrumento de medición que en este caso es un metro cuyo error es $\frac{+}{-} 1 mm$, el error en la medida de la corriente es de $\frac{+}{-} 1 mA$.\\

\begin{thebibliography}{99}
\bibitem{ARDUINO} Arduino, pagina oficial, proyecto arduino. http://www.arduino.cc/
\bibitem{REGULADOR} Hoja de datos  transistor lm 7805CV. http://pdf.datasheetcatalog.net/datasheet/fairchild/\\LM7805.pdf
\bibitem{TIP122} Hoja de datos del transistor tip 122. http://pdf.datasheetcatalog.net/datasheet/fairchild/\\TIP122.pdf.
\bibitem{DIODO}  Hoja de datos diodo regulador 1N4001. http://pdf.datasheetcatalog.net/datasheet/lrc/\\1N4001.pdf
\bibitem{INFRARED} Hoja de datos de los diodos led infrarrojos, emisor y receptor. \\ http://www.datasheetarchive.com/dlmain/Datasheets\\-31/DSA-617614.pdf
\bibitem{FRITZING} Pagina oficial del proyecto fritzing http://fritzing.org/home/ 
\bibitem{PYTHON} Notas del curso, python para el computo científico, curso de actualización académica de la DGAPA-UNAM, Facultad de ciencias, Dr. David P. Sanders, 5 de agosto de 2013. 
\bibitem{CIRCUITOS} Fundamentos de circuitos eléctricos, tercera edición, editorial Mc Graw Hill, Charles K. Alexander and Matthew N. O. Sadiku. 
\bibitem{BERKELEY} Berkeley Physics Course, volumen 3, Ondas (Crawford).
\bibitem{HECHT} Óptica, Eugene Hecht, tercera edición
\end{thebibliography}
\end{multicols}
\end{document}

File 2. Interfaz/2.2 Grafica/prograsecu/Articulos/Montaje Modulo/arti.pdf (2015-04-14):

Montaje de un modulo motorizado, con sensores infrarrojos,

# controlado con una tarjeta atmega 328P-PU y comunicaci´on

serial v´ıa bluetooth en un ordenador con GNU-Linux.

Diego Alberto Parra Garz´on ∗ Universidad Distrital, Calle 3 No 26A-40 Bogot´a-Colombia Proyecto Curricular de Licenciatura en F´ısica

April 13, 2015

Abstract
It is necessary to visualize the extent that free technologies have today about the company, these technologies are the foundation of the economy of many countries, and why not say that it has reached an age where information and means to transmit they are available to anyone, such is the case we can take this technology and make it new tools to support the work of science teaching and learning in science, for this reason it has decided to take this whole world of free technologies, combine them and make it these new tools we need to continue this work of learning and teaching that never ends.

illustrating the attenuation property with electromagnetic waves; as the wavelengths in the infrared are also part of the electromagnetic spectrum and everyday use we give to this radiation is very wide, so it is essential to place this resource for both students and professionals, for the experimental part is combined with the theoretical giving a feedback issue. Data were obtained from a motor module equipped with an infrared sensor receiver and an infrared LED emitter, which are controlled by a atmega microcontroller 328-Pu and this is linked via Bluetooth to a computer, this process is done by the computer with the help of free software like python, gnuplot, octave among other languages, it is worth noting that everything is done in a free operating system like linux mint or debian. Data analysis laboratory, which will have to shed the value of attenuation of electromagnetic waves and has to mat.
Keywords: Motor module, infrared sensors, microcontroller module bluetooth, electromagnetic wave.

Resumen

Es necesario visualizar el alcance que las tecnolog´ıas libres tienen el d´ıa de hoy sobre la sociedad, estas tecnolog´ıas son las bases de las econom´ıas de muchos pa´ıses, y porque no decirlo que se ha alcanzado una era en donde la informaci´on y los medios que la transmiten est´an al alcance de cualquier persona, tal es el caso que podemos tomar esta tecnolog´ıa y hacer de ella nuevos instrumentos que respalden la labor de la ense˜nanza cient´ıfica y el aprendizaje en ciencias, por esta raz´on se ha decidido tomar todo este mundo de tecnolog´ıas libres, combinarlas y hacer de ella esos nuevos instrumentos que necesitamos para continuar con esta labor de aprendizaje y ense˜nanza que no termina nunca.

Este articulo espera ser acogido por estudiantes y profesionales que vean en este un modelo did´actico, con materiales que consiguen f´acilmente y con un gran poder de exactitud en las mediciones; en este se ilustra un montaje experimental, de un modulo motorizado o en otras palabras un dispositivo m´ovil impulsado por un motor en este caso el´ectrico; est´a equipado con un microcontrolador atmega 328P-PU, este se encargara de toda la parte de control de los dem´as elementos el´ectricos, dispondr´a de dos diodos led receptores en el infrarrojo de GaAs, tambi´en consta de un diodo led emisor en el infrarrojo de GaAs, un modulo bluetooth hc-06 para arduino y una bater´ıa de 9 voltios junto con un regulador de 9V a 5V. Todo esto con el fin de poder hacer mediciones de la intensidad de la radiaci´on producida por estos diodos y calibrar el dispositivo para aplicaciones ilustrativas de las propiedades de las ondas electromagn´eticas y su dualidad onda – part´ıcula.
Descriptores: | Modulo | motorizado, | sensores | infrarrojos, | microcontrolador, | modulo | bluetooth, | ondas
electromagn´eticas.

∗diegoestudianteud1@gmail.com

## 1 Introducci´on

Al no poderse descartar la realidad de las tecnolog´ıas libres, su r´apido crecimiento y el hecho de que sean muy sencillas de utilizar, ha sido el detonante para la realizaci´on de este proyecto; el cual pretende elaborar un sistema electr´onico-mec´anico que sea controlado v´ıa bluetooth, sin necesidad de un sistema f´ısico de cables; este debe tener la cualidad de ser lo m´as exacto posible en cuanto a la captura y manipulaci´on de datos; sin dejar a un lado su bajo costo.

Tambi´en tiene la pretensi´on de ser un modelo did´actico, que pueda ser utilizado en la ense˜nanza de la ciencia de una manera practica, llamativa, con la cual el estudiante pueda tener una sensaci´on de que las ciencias son divertidas, sin dejar de lado su exactitud y su car´acter de buscar el ¿por qu´e?, los ¿c´omo?, y la precisi´on al compararse la teor´ıa con la parte experimental.

## 2 Configuraci´on experimental

### 2.1 Materiales para el montaje

Para la realizaci´on de este montaje se utilizaron los siguientes materiales:

a. Un ordenador con un sistema operativo GNU-Linux.
b. Microcontrolador atmega 328P-PU [1] para realizar la parte de control del hardware.
c. Dos diodos led infrarrojos[5] receptores.
d. Un diodo led infrarrojo[5] emisor.
e. Un motor a 9 voltios DC, junto con un transistor TIP 122[3] para el control de la velocidad de giro del engranaje del motor.
f. Modulo Bluetooth HC-06 para arduino, el cual permita la comunicaci´on a distancia con el dispositivo, sin necesidad de un sistema f´ısico cableado.
g. Transistor LM-7805CV [2] para un transformador de voltaje de 9 voltios a 5 voltios el cual alimentara el microcontrolador atmega328P-PU, y los dem´as dispositivos del proyecto.
h. Un cristal de 16 MHz.
i. Tarjeta arduino [1] uno.
j. Tres resistencias de 220 ohms a 500 ohms.
h. Dos resistencia de 500 ohms.
i. Tres resistencias de 1 komhs.
j. Diodo rectificador de referencia 1N4001. [4]
k. Dos capacitores cer´amicos de 12 picofaradios.
l. Dos capacitores de 10 microfaradios.
m. Sistema de engranajes de eje m´ovil, para realizar el movimiento del veh´ıculo.
n. Cuatro llantas de carros de juguetes.

˜n. Una bater´ıa de 9 V.

o. Una tabla o un acr´ılico de 14x12x0.3 cm³
p. Un interruptor peque˜no.

### 2.2 Montaje experimental

### 2.2.1 Circuito electr´onico

A continuaci´on se explica paso a paso como armar el circuito el´ectrico, el montaje se realiza en fritzing¹
. Se explicara
parte por parte del circuito y luego todas deben unirse en una sola.

Cabe mencionar que los esquemas de las figuras de la 1 a la 8 fueron tomadas de la pagina principal del proyecto arduino[1], y modificadas en fritzing[6]

Lo primero que se har´a, sera preparar el microcontrolador para su primer uso, debido a que los microcontroladores atmega 328 P-PU no vienen listos para comenzar a programar; es necesario hacer un stand alone²
sobre el
microcontrolador.

1Enlace a la pagina oficial del proyecto fritzing http://www.fritzing.org/home/
2Enlace a un bootloader https://arduinoelectronics.wordpress.com/2012/02/10/standalone-atmega-without-arduino-bootloader/

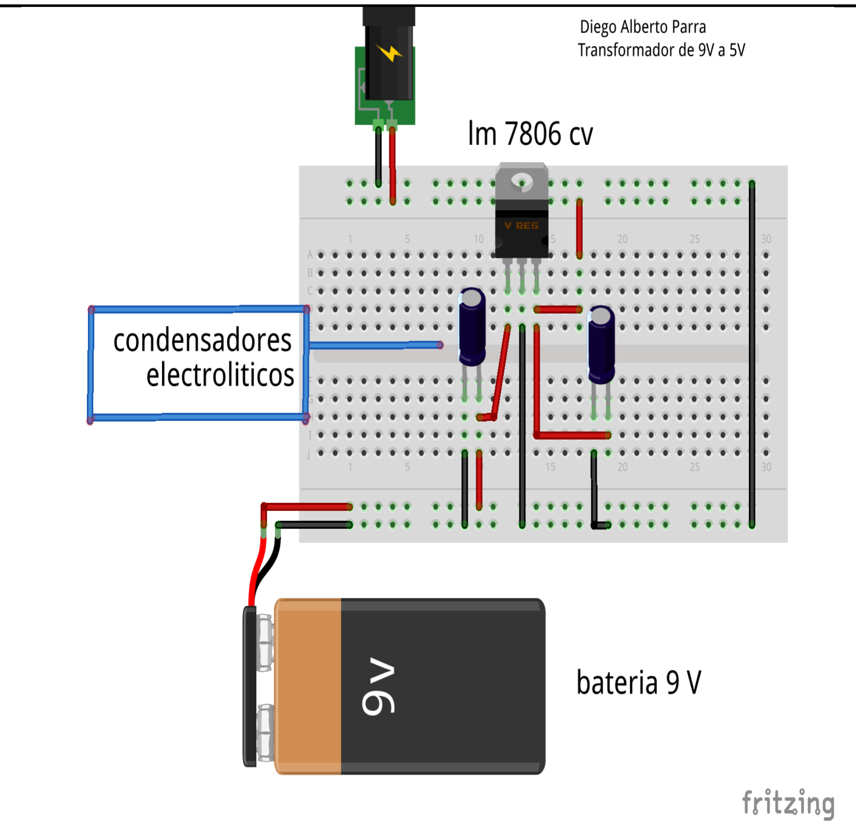
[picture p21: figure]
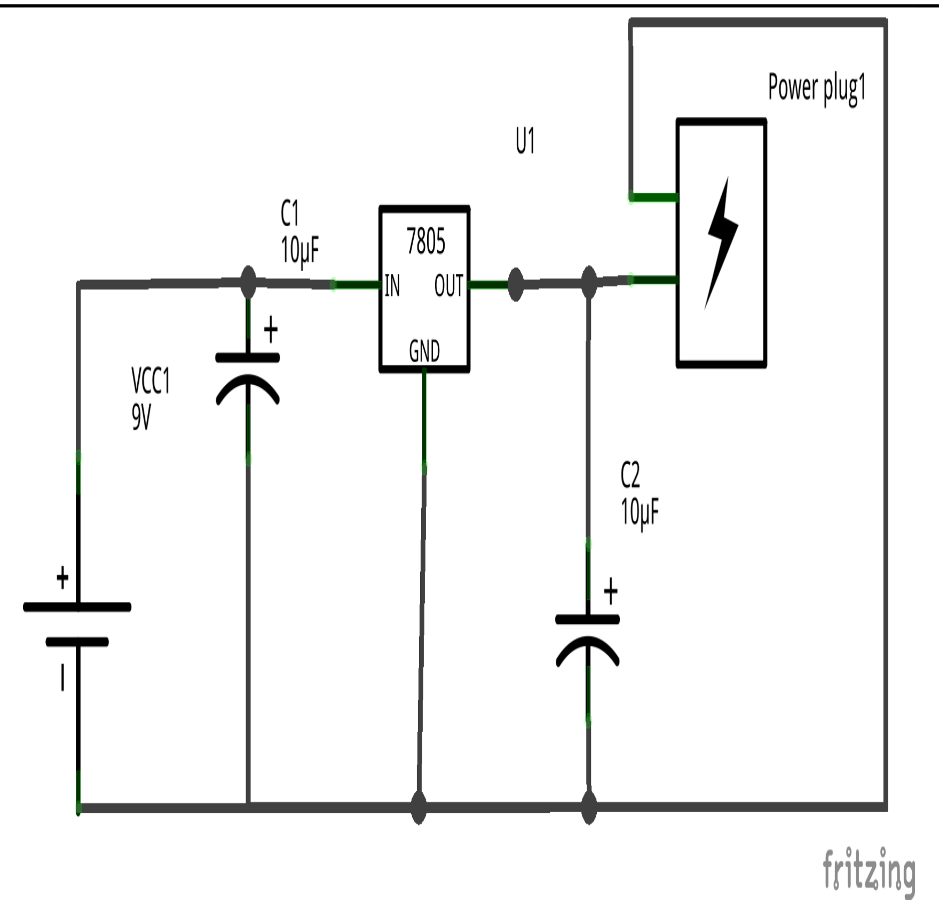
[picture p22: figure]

1.A. | 1.B

Figure 1: En la figura 1.A. se observa el esquema el´ectrico de un transformador [2] de 9V a 5V, utilizando un transistor lm 7805 cv. Los capacitores son electrol´ıticos de 10 microfaradios. En la figura 1.B. se observa el montaje en protoboard del circuito regulador.

Montamos un transformador de 9 voltios a 5 voltios, esto lo hacemos con dos capacitores electrol´ıticos de 10 microfaradios y el transistor lm7805[2] cv. Ambos capacitores deben ir en paralelo quedando su extremo negativo conectado a tierra y su extremo positivo uno a la entrada de 9 V y el otro a la salida de 5 V del transistor, el transistor lm consta de 3 pines uno de los cuales es la entrada de +9V, el pin de la mitad es tierra o GND y el pin extremo es la salida a 5V; tal como se muestra en la figura 1.A.; en la figura 1.B. se le coloco un enchufe de salida de poder. El modulo bluetooth se debe conectar de la siguiente manera: el pin 2 de la tarjeta arduino es el Rx este va conectado al Tx del blueetooth, el pin 3 del microcontrolador es el Tx y va conectado al pin Rx del bluetooth, como se muestra en la figura 2.A y 2.B , conectamos el GND del bluetooth al pin 8 o 16 de nuestro microcontrolador , ahora conectamos el pin de Vcc del bluetooth al pin 7 o 14 del microcontrolador.

Necesitamos colocar un oscilador de 16 mHz el cual lo dejaremos siempre en el microcontrolador, esto con el fin de ajustar los tres relojes internos que trae nuestro integrado atmega 328 P-Pu, para esto utilizamos el cristal de 16 mHz junto con los dos condensadores cer´amicos de 12 picofaradios 3
, uno de los pines del cristal debe conectarse al pin 9 del microcontrolador y el otro extremo del cristal al pin 10, conectamos un capacitor a cada extremo del cristal y estos al pin 8 o 16 del microcontrolador de tal forma que los capacitores quedan en paralelo.
Colocamos | un | bot´on⁴ | para | reiniciar | nuestro
microcontrolador en caso de que lo necesitamos, esto lo hacemos colocando uno de los extremos del bot´on al pin 1 del microcontrolador que es el pin de reset, el otro extremo del bot´on lo conectamos a una resistencia de 1 Komhs y el extremo de la resistencia a tierra.

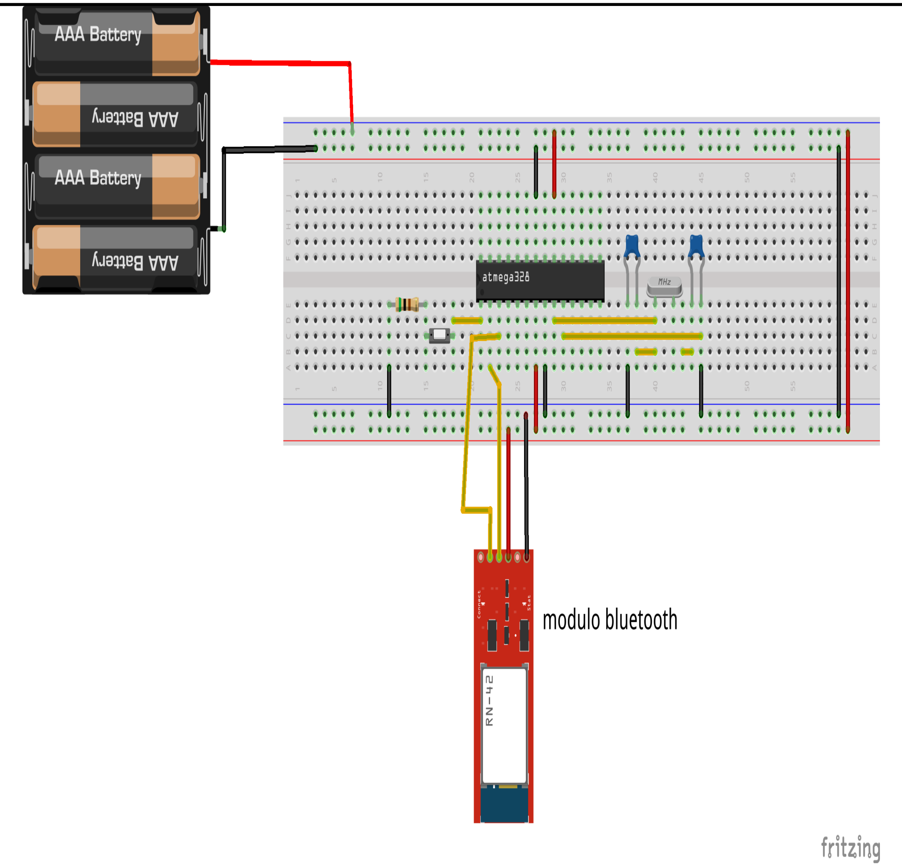
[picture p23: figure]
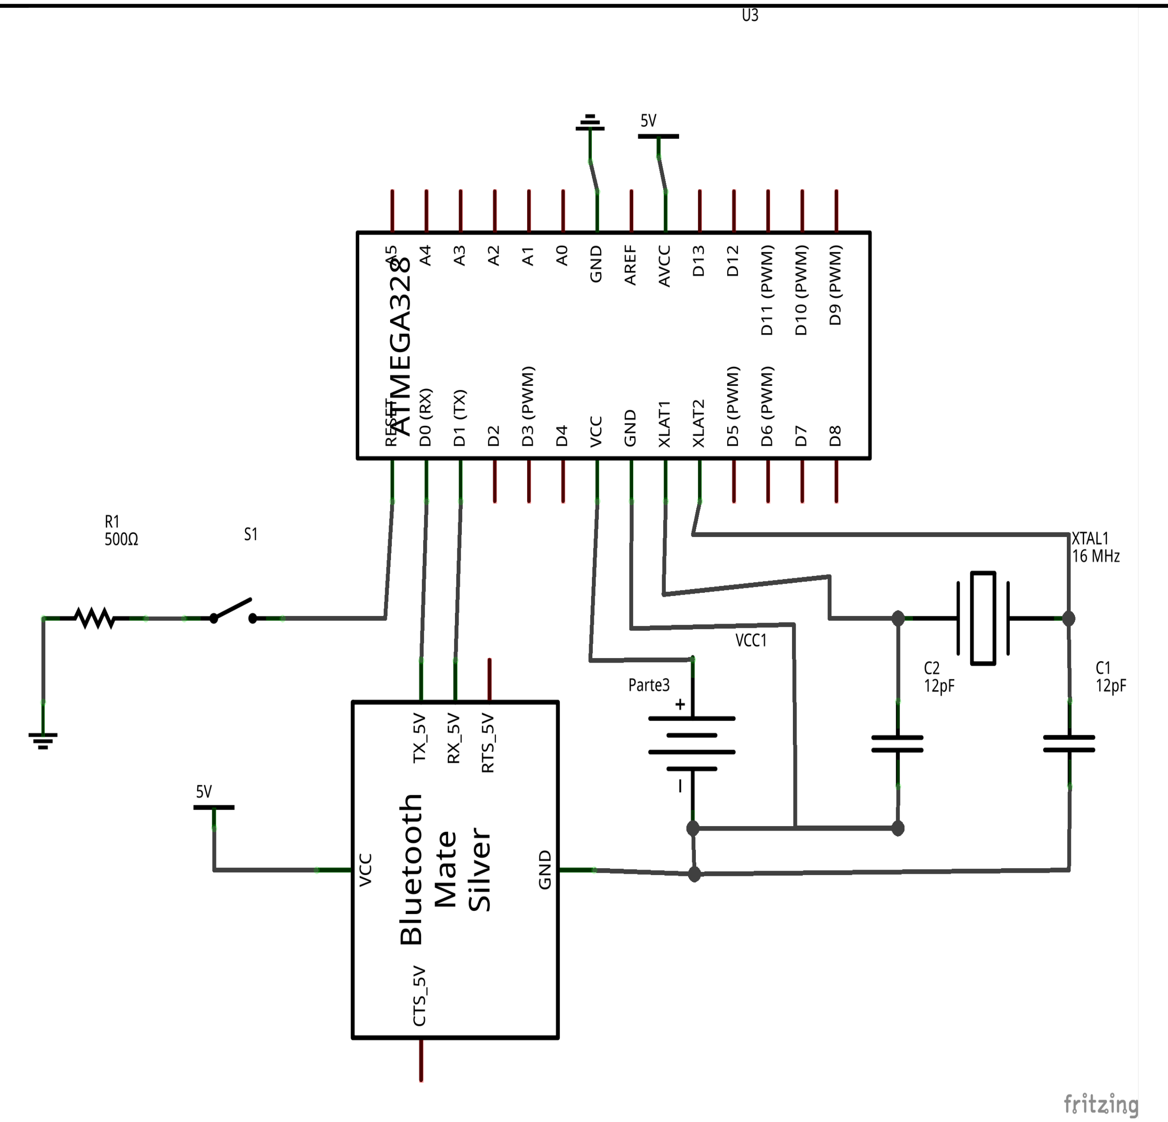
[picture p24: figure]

2.A. | 2.B.

Figure 2: En la figura 2.A se muestra el circuito el´ectrico de un bluetooth conectado a un microcontrolador atmega 328 P-PU junto con un cristal, dos capacitores cer´amicos, un bot´on de reset y una resistencia de 1 Komhs. En la figura 2.B esta el montaje en protoboard, los cables negros son tierra, los cables rojos son voltaje, y los cables amarillos son conexiones.

Las conexiones del motor son las siguientes, como vamos a utilizar un transistor tip[3] 122, los pines mostrados en la figura 2.B. est´an de la siguiente manera:

* El pin del lado izquierdo del transistor es la base.

* El pin del centro es el colector.

* El pin de la derecha es el emisor.

Conectamos una resistencia de 1 kΩ al pin base del transistor y este a su vez al pin numero 5 del integrado
atmega328P-PU⁵ | , luego conectamos el pin del colector del
tip122 a +5V, asegur´andonos de colocar el diodo regulador entre el colector y uno de los extremos del motor; a continuaci´on conectamos el pin emisor del transistor junto con el otro extremo de la conexi´on del motor a tierra; ahora colocamos las conexiones del condensador cer´amico entre las conexiones del motor.⁶

3Ver figura 2.A y 2.B.
4Como se muestra en la figura 2.A y 2.B. 5Como se aprecia en la figura 2.B. 6Observar figuras 2.A. y 2.B.

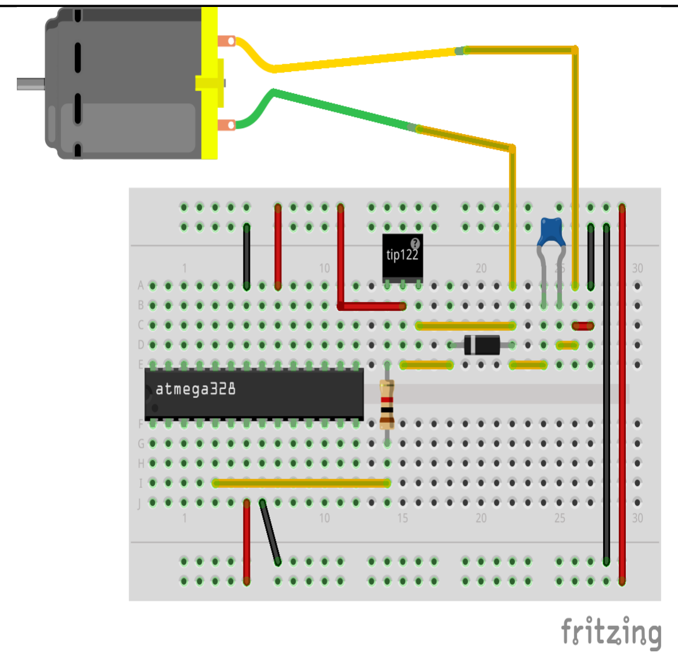
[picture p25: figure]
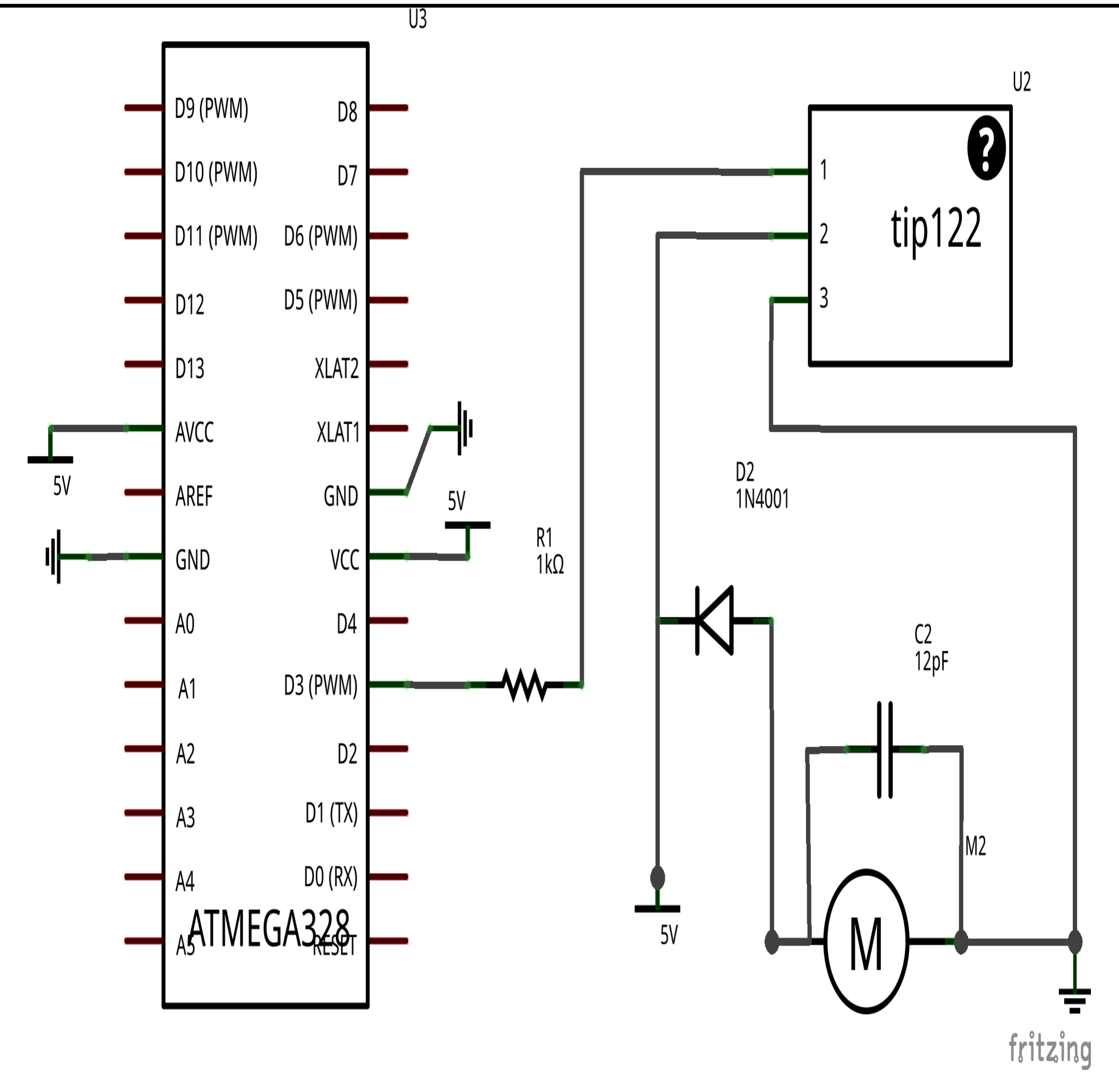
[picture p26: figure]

3.A. | 3.B.

Figure 3: En la figura 3.A se muestra el circuito el´ectrico del motor conectado a la tarjeta atmega 328 P-PU, junto con un tip 122 encargado de controlar la corriente que circula por el motor consiguiendo de esta manera controlar la velocidad de este, tambi´en lleva un diodo regulador, un capacitor cer´amico de 12 picofaradios y una resistencia de 1 Komhs. En la figura 3.B esta el montaje en protoboard, los cables negros son tierra, los cables rojos son voltaje, y los cables naranjas son conexiones.

Procedemos hacer las conexiones del sensor receptor lateral 7
el cual es un diodo led receptor de luz infrarroja [5], conectamos una resistencia de 1kΩ al ´anodo del led y el otro extremo de la resistencia a tierra, luego conectamos el pin 28 8 del microcontrolador en un punto intermedio entre la resistencia y el ´anodo del diodo led, el c´atodo del diodo lo conectamos a +5V.

Para las conexiones del sensor receptor frontal 9
el cual
es un diodo led receptor de luz infrarroja [5], conectamos una resistencia de 1kΩ al ´anodo del led y el otro extremo de la resistencia a tierra, luego conectamos el pin 22 10 del microcontrolador en un punto intermedio entre la resistencia y el ´anodo del diodo led, el c´atodo del diodo lo conectamos a +5V.

Para la conexi´on de la fuente¹¹ emisora de fotones infrarrojos o radiaci´on infrarroja se utiliza un diodo led emisor en el infrarrojo, el c´atodo del diodo lo conectamos a una resistencia de 350Ω a 500Ω y el otro extremo de la resistencia lo conectamos a tierra, el ´anodo del diodo lo conectamos al pin 12¹² del microcontrolador.

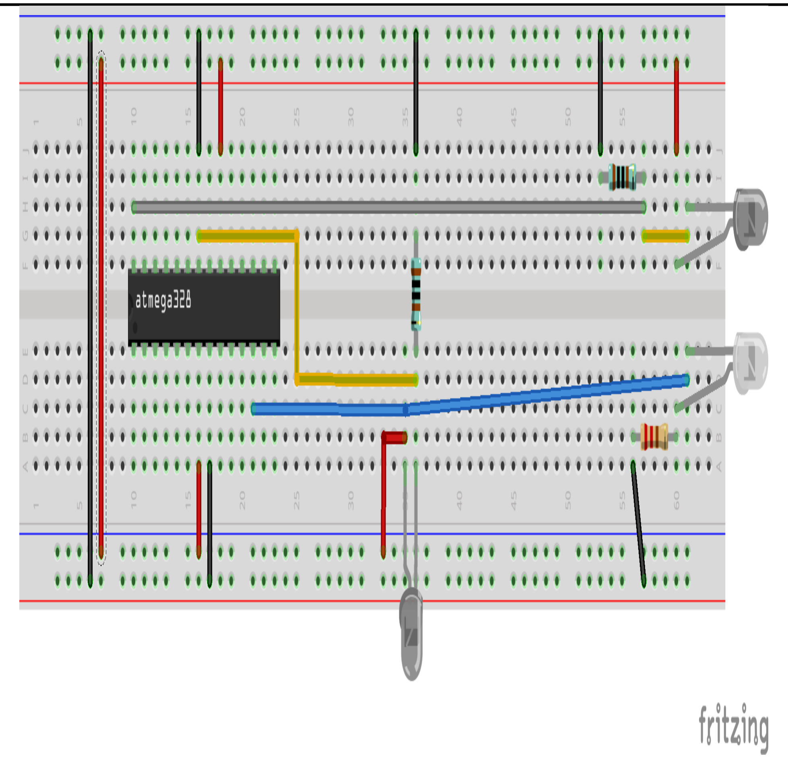
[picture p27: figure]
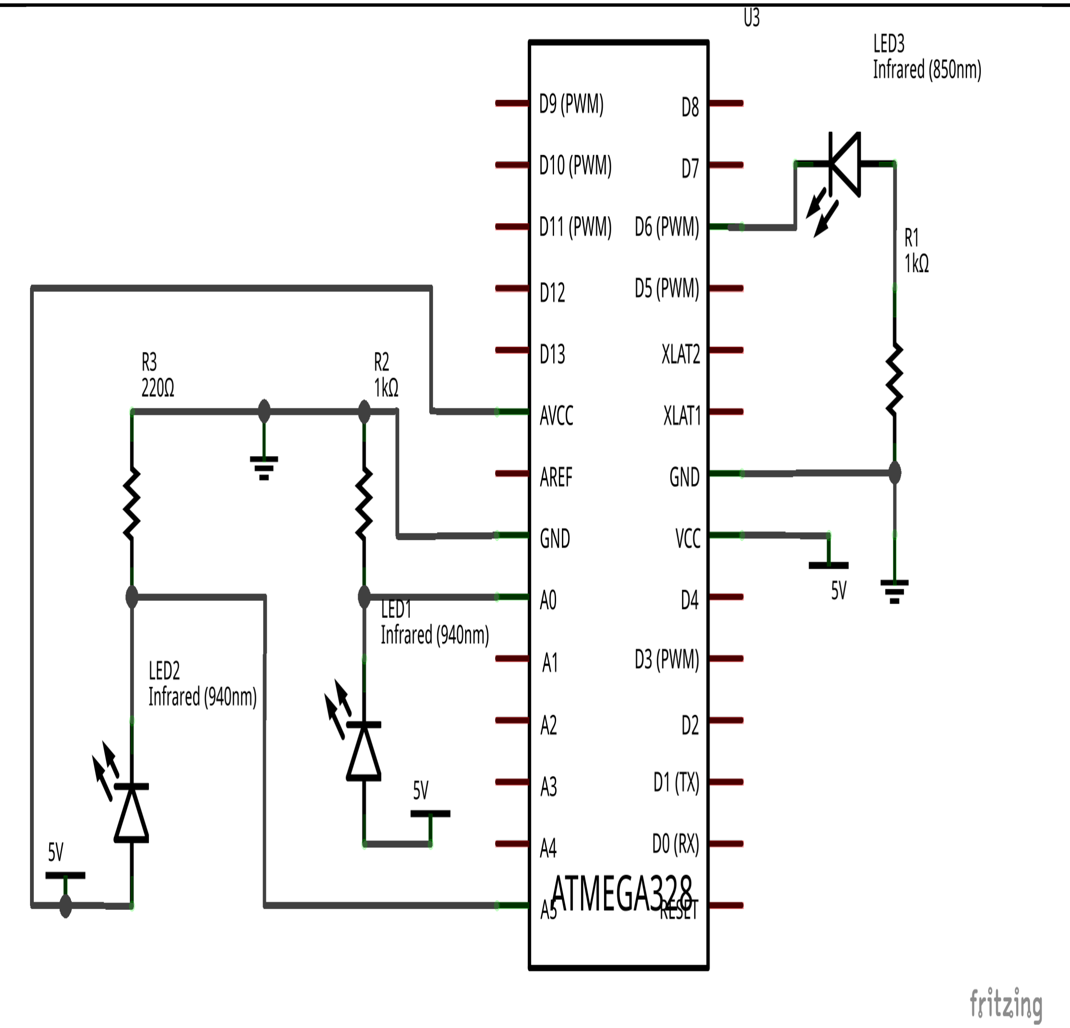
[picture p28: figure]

4.A. | 4.B.

Figure 4: En la figura 4.A se observa las conexiones de los diodos tanto receptores como el emisor, conectamos al microcontrolador atmega328P-PU. En la figura 4.B esta el montaje en protoboard, los cables negros son tierra, los cables rojos son voltaje, el cable azul es la conexi´on entre el ´anodo del diodo led emisor infrarrojo frontal y el pin 6 del microcontrolador, el cable naranja es la conexi´on entre el pin 23 del microcontrolador y el punto de conexi´on entre el ´anodo del diodo receptor infrarrojo lateral con la resistencia, el cable gris es la conexi´on entre el pin 28 del microcontrolador y el punto de conexi´on entre el ´anodo del diodo receptor infrarrojo frontal con la resistencia.

Las conexiones¹³ del diodo rgb de ´anodo com´un es la siguiente: conectamos el ´anodo del diodo rgb a +5V, el pin rojo del diodo rgb lo conectamos a una resistencia de 500Ω y el otro extremo de la resistencia conectado al pin 18 del microcontrolador, el pin verde del diodo rgb lo conectamos a una resistencia de 500Ω y el otro extremo de la resistencia conectado al pin 16 del microcontrolador, el pin azul del diodo rgb lo conectamos a una resistencia de 500Ω y el otro extremo de la resistencia conectado al pin 15 del microcontrolador.

Una vez terminadas las conexiones solo resta soldarlas en una baquela. Por ultimo pero no menos importante es conseguir icopor y hacer unas bases para que en ellas repose nuestro circuito de esta manera nos aseguramos en caso de cualquier incidente que las placas no se vayan a estropear ni que las conexiones vayan a quedar haciendo corto.

7Se aprecia en la figura 4.A. y en la figura 4.B.
8Este pin es la entrada anal´ogica numero cero del microcontrolador atmega.
9Se aprecia en la figura 4.A. y en la figura 4.B., en la parte donde est´an los dos diodos led. 10Este pin es la entrada anal´ogica numero cinco del microcontrolador atmega.
11Ver figura 4.B. y su esquema en la figura 4.A.
12Salida D6 PWM.
13Ver los esquemas de la figura 5.A. y 5.B.

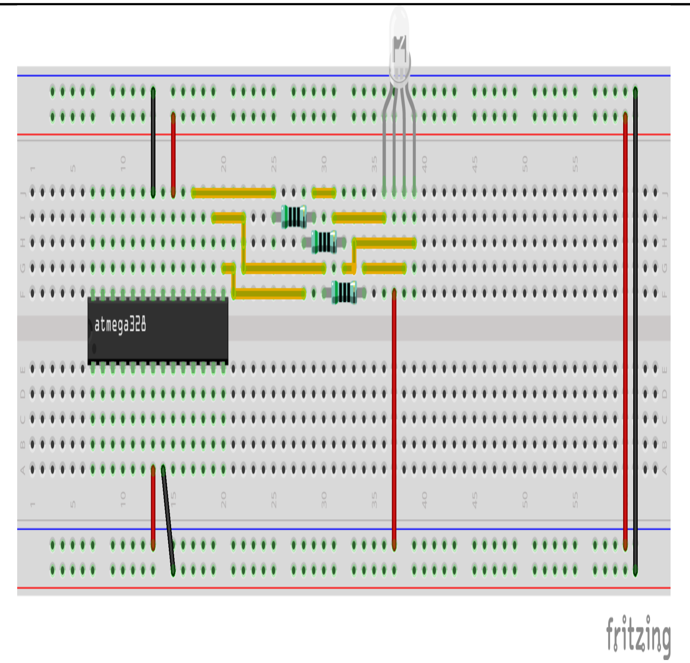
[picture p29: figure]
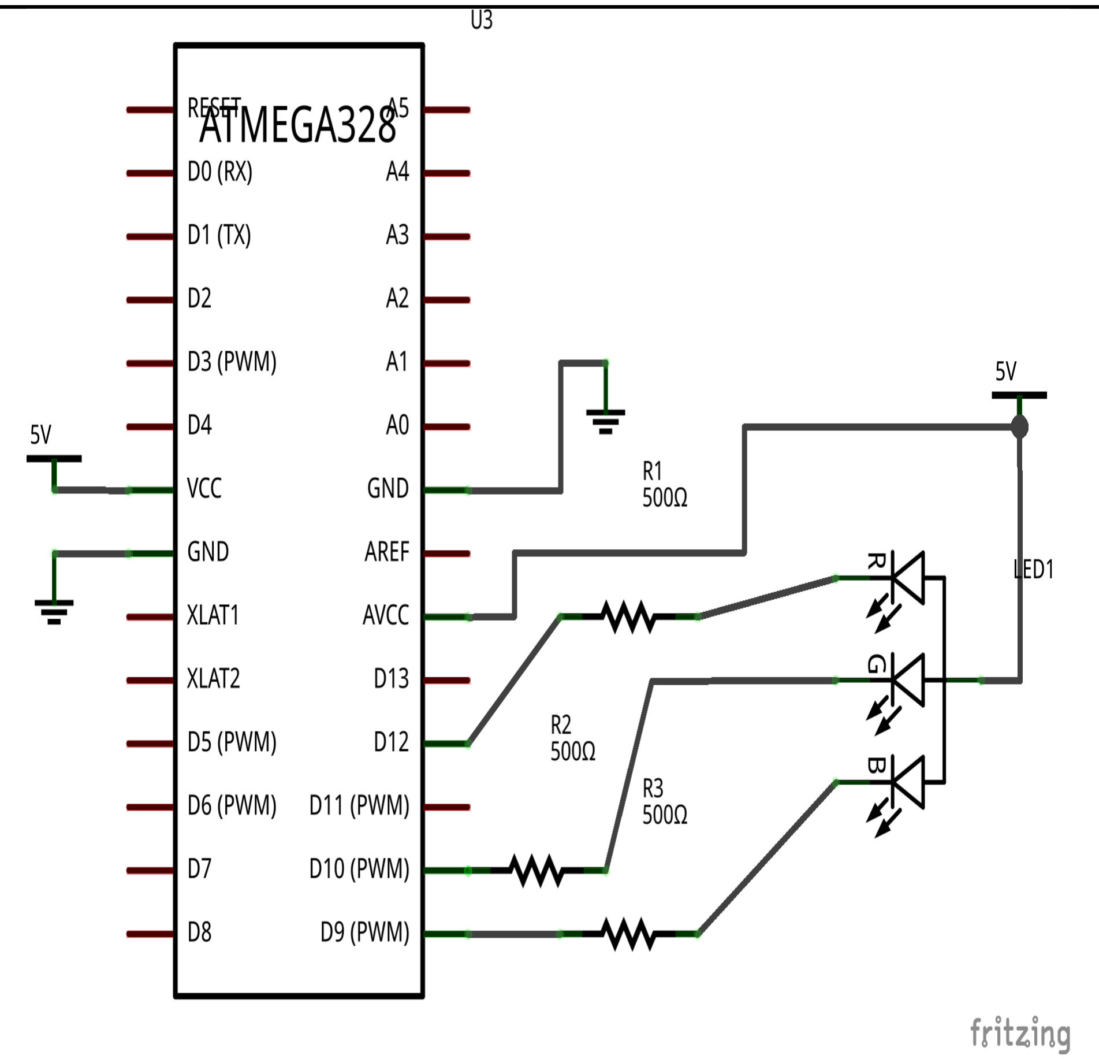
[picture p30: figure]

5.A. | 5.B.

Figure 5: En la figura 5.A. se muestra el circuito el´ectrico del diodo rgb conectado al microcontrolador atmega 328 P-PU. En la figura 5.B esta el esquema del diodo rgb en protoboard.

Esa era la parte el´ectrica ahora los esquemas el´ectricos deben unirse para formar un solo circuito¹⁴, antes de soldar el microcontrolador atmega 328P-PU es necesario cargar el archivo de control del hardware, cuyos pasos son los siguientes:

a. Instalar git 15
b. Descargar el repositorio de este proyecto 16
c. Una vez descargado el repositorio hay que ir desde la terminal de linux a la carpeta donde se encuentra alojado el repositorio que acaba de descargar; si usted clono el repositorio en su carpeta home, solo coloque la siguiente linea en una terminal sin la primera y ultima comilla “cd ”Modulo Motorizado/0. Instalaci´on/0.1 programas requeridos/””.
d. Acceda como usuario root y a continuaci´on escriba en la terminal la siguiente linea sin las comillas “python install.py”, se abrir´a el programa de instalaci´on del proyecto, ahora siga las instrucciones del programa.
e. Al terminar el programa le pedira si desea reiniciar el ordenador, escriba n y luego presione enter.
f. Escriba sin las comillas “exit” y oprima enter, luego escriba “arduino” y oprima enter, abrir´a una ventana donde debe seleccionar la opci´on add. Luego de esto vera la IDE de arduino, ci´errela y reinicie el ordenador.
g. Desde nuestro navegador de archivos del sistema¹⁷ entramos a la carpeta Modulo Motorizado/1. Inicio/ 1.2 programar arduino y sensores, all´ı encontraremos el archivo sensores2.ino, lo seleccionamos y oprimimos enter.
h. Conectamos | la | tarjeta | arduino junto | con | el
microcontrolador que vamos a dejar en el proyecto, en la IDE de arduino vamos a la opci´on herramientas,
tarjeta | y | seleccionamos | arduino | uno; | ahora
nuevamente en herramientas, damos click en puerto serial y seleccionamos el puerto que nos aparece, ahora oprimimos la tecla ctrl y la tecla “u” 18 al mismo tiempo y esperamos mientras carga el sketch, una vez cargado retiramos el microcontrolador y lo colocamos en la parte del proyecto donde se le dispuso su sitio.

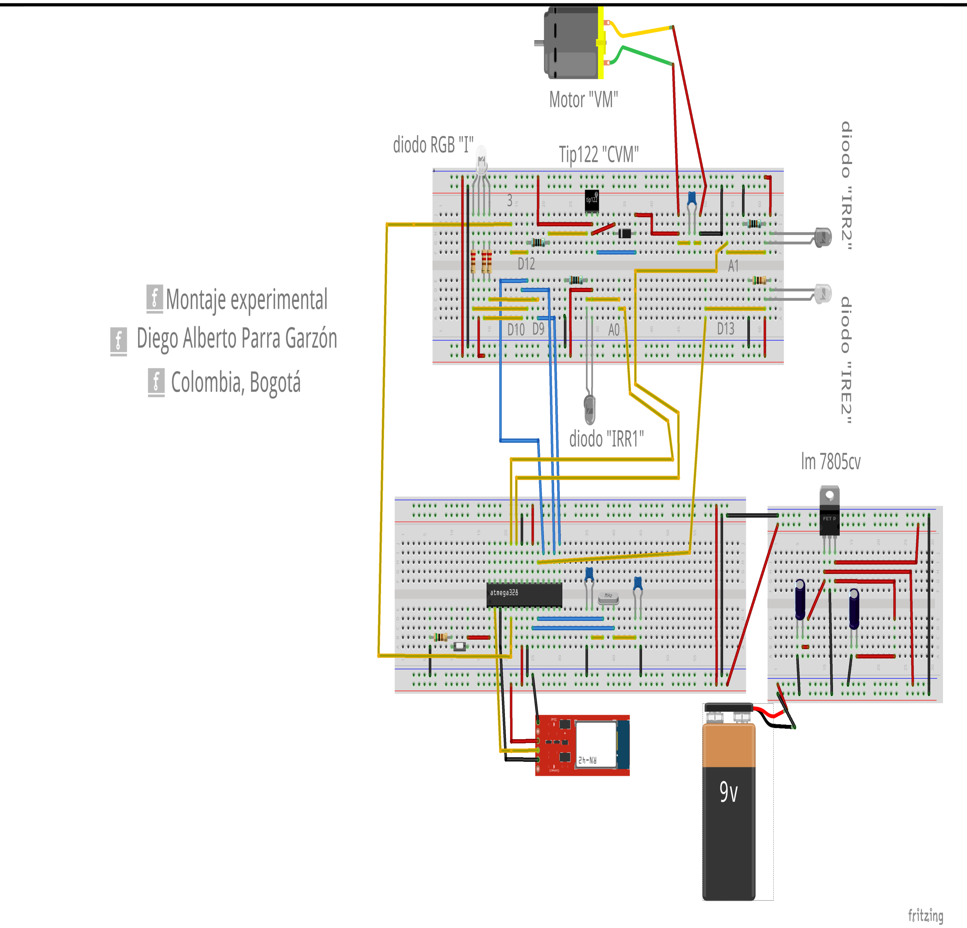
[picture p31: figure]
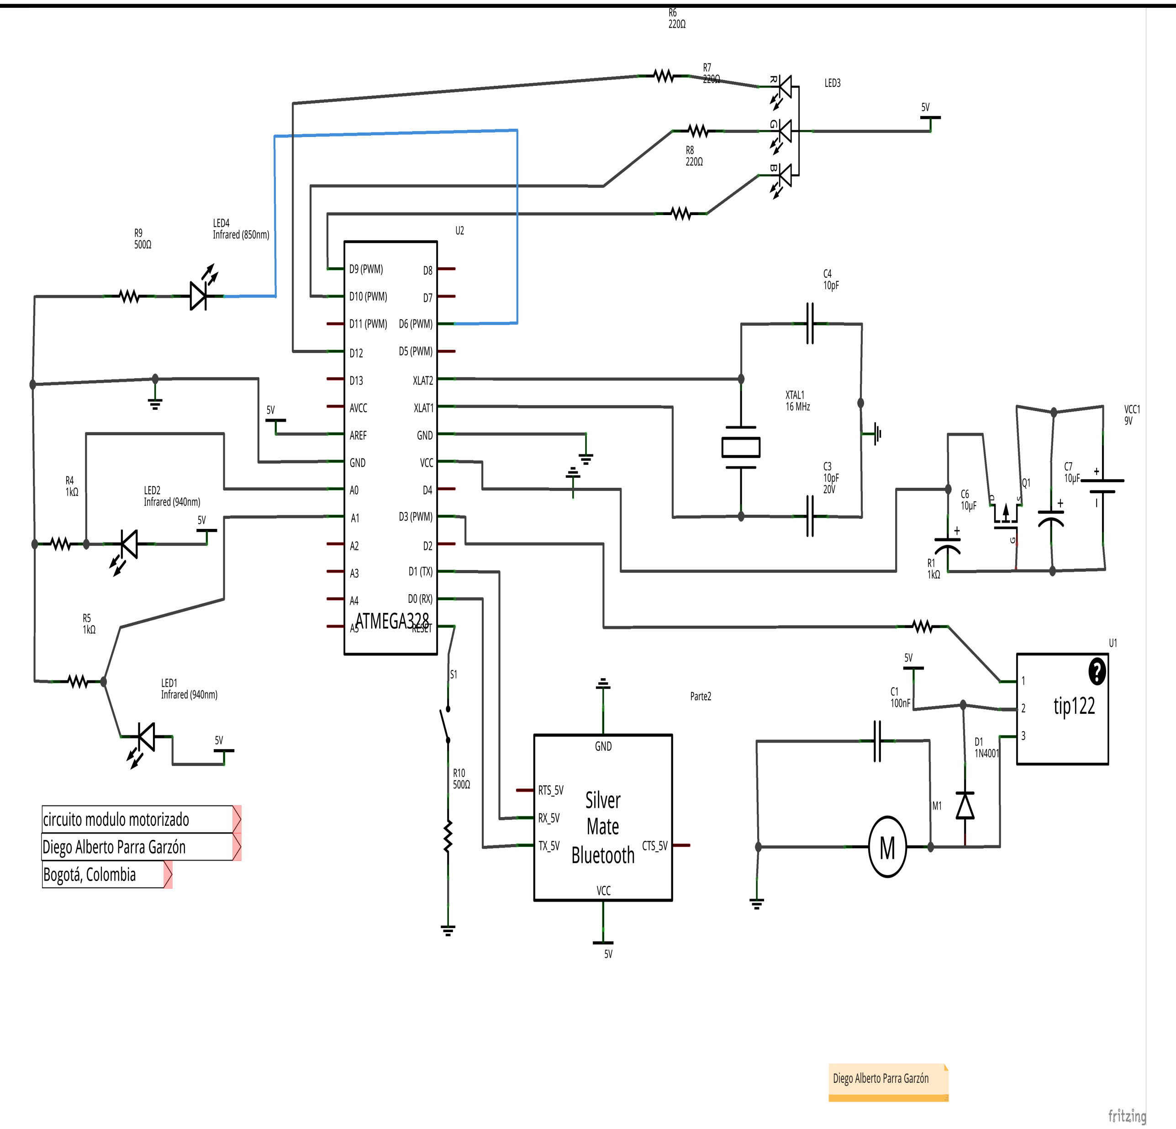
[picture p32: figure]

6.A. | 6.B.

Figure 6: En la figura 6.A. se muestra el circuito el´ectrico del proyecto. En la figura 5.B esta el esquema del proyecto.

### 2.2.1 Montaje mec´anico

Lo primero sera tomar la tabla de madera o acr´ılico y hacer un chasis como el que aparece en la figura 7, para montar nuestro sistema de transmisi´on¹⁹, el circuito el´ectrico, y el sistema de rodamiento delantero²⁰

14Ver figura 6.A., y 6.B.
15Enlace para instalar git http://git-scm.com/download/linux
16En una terminal escribimos git clone https://github.com/Diego-debian/Modulo Motorizado.git 17Puede estar utilizando los siguientes en su distribuci´on linux, nautilus, thunar o alg´un otro. 18Sin las comillas.
19Ver figura 8.B.
20Ver figura 8.A. y 8.B.

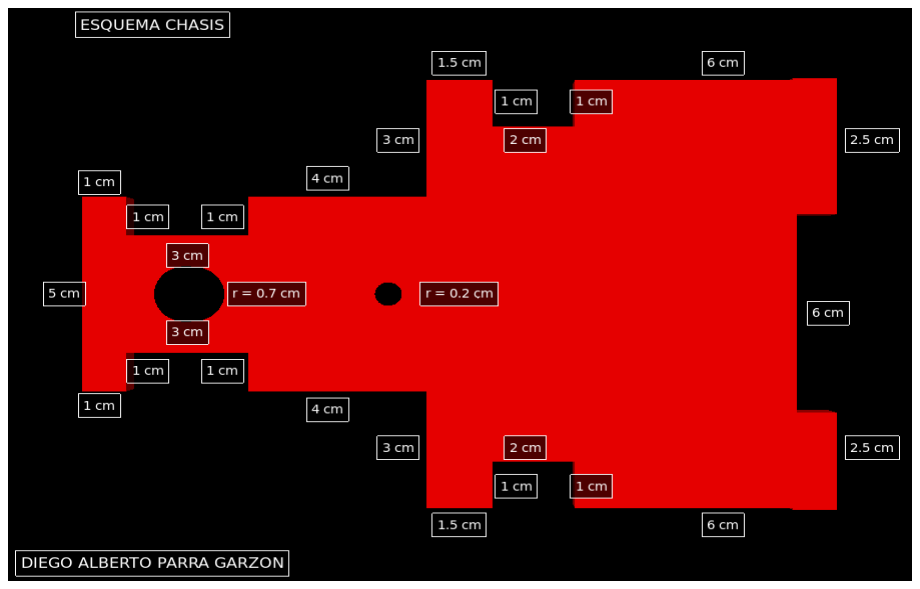
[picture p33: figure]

Figure 7: En esta figura se observan las dimensiones del chasis que va servir de base del circuito el´ectrico y donde reposara el sistema de transmisi´on del proyecto. Esta figura fue modelada en python visual.

Ahora colocamos las llantas del veh´ıculo para esto colocamos dos llantas de 1.5 cm de radio en el eje delantero y luego colocamos dos llantas de 2.5 cm de radio en los ejes traseros; esto con el fin de reducir la rapidez angular de las llantas, la cual se manifestara en una disminuci´on significativa de la rapidez del veh´ıculo.

Despu´es de tener todo montado como se aprecia en la figura 9, hemos terminado toda la parte del montaje del modulo motorizado.

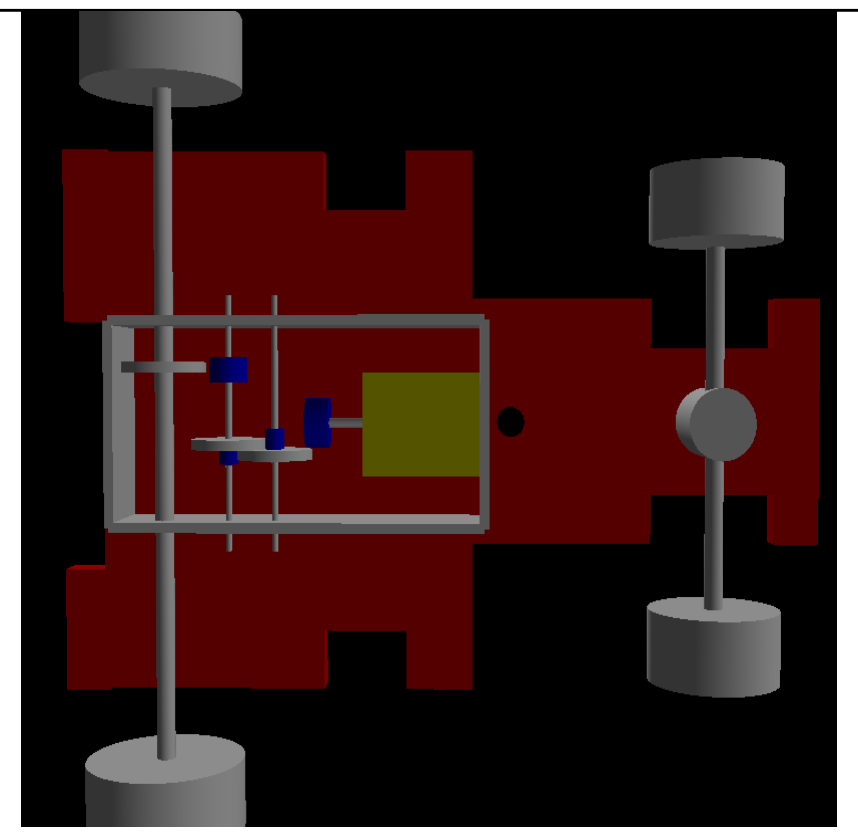
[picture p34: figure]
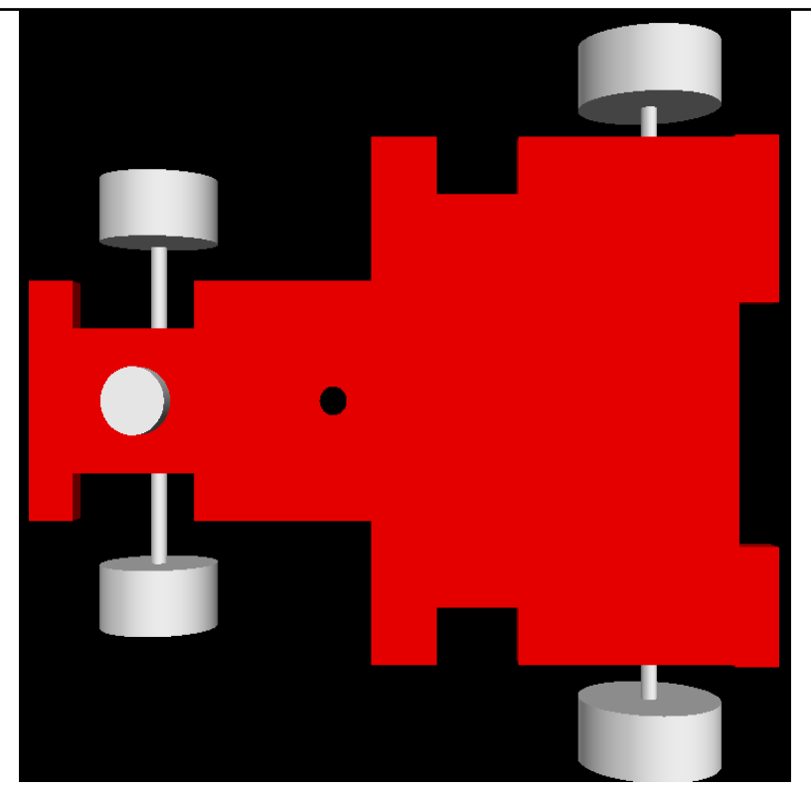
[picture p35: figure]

8.A. | 8.B.

Figure 8: En la figura 8.A. se muestra la vista superior del montaje del veh´ıculo motorizado, solo falta colocar la parte el´ectrica. En la figura 8.B se muestra el montaje del veh´ıculo motorizado con una vista inferior, junto al sistema de transmisi´on, y el rodamiento delantero. Las figuras fueron modeladas en python visual.

Este veh´ıculo se encuentra en una etapa alpha, de esta manera hace falta montar toda la parte est´etica del veh´ıculo, esto se deja a disposici´on de cada persona, pues lo realmente importante del veh´ıculo es sus funciones, pero no hay que olvidar que la parte est´etica es y sera muy importante si este producto quisiera comercializarse.

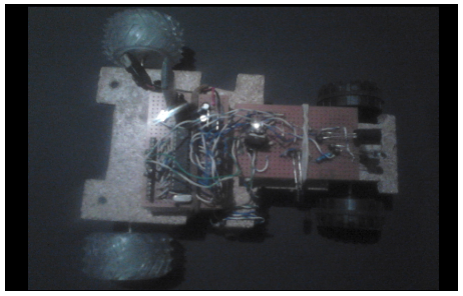
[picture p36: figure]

Figure 9: Este es el montaje final del vehiculo motorizado.

## 3 Experiencia de laboratorio

Una vez descargado nuestro repositorio del proyecto, y teniendo listo el montaje del mismo, es necesario hacer las respectivas pruebas de rapidez e intensidad de radiaci´on del veh´ıculo, para poder realizar estos an´alisis fue necesario crear una interfaz gr´afica en python[7] que fuera capaz de controlar el veh´ıculo, obtener datos de este y hacer sus respectivos an´alisis.

### 3.1 Pruebas de rapidez

Lo | primero | que | debemos | hacer | es | desde | una
terminal dirigirnos hasta la carpeta donde hemos
descargado nuestro repositorio, | luego escribimos cd
“Modulo Motorizado/2. | Interfaz/2.2 Grafica”; | ahora
escribimos python Gverificar.py y oprimimos enter, nos debe aparecer la interfaz gr´afica de bienvenida, en la que encontraremos una imagen con nuestro veh´ıculo, damos click en la imagen e inmediatamente se nos abrir´a otra ventana en donde encontraremos las opciones que necesitamos, damos click en la opci´on que dice prueba 1, esto nos abrir´a otra ventana en la que nos pide la ruta al dispositivo, para esto escribimos en la terminal blueman-manager, damos al icono de la lupa y nos buscara los dispositivos bluetooth disponibles, apenas veamos nuestro modulo bluetooth, que por lo general siempre aparece como HC-06 o HC-05, damos click derecho sobre este, seleccionamos la opci´on de emparejar y escribimos la clave de paso, por default es 1234; ahora una vez emparejado procedemos hacer click derecho nuevamente sobre el dispositivo y damos click en la opci´on “dev B”, si todo sale bien nos dar´a v´ıa libre al puerto serial y nos dir´a la ruta al dispositivo; una vez tengamos el nombre de la ruta al dispositivo la escribimos en la ventana de nuestro programa y damos enter²¹, a lo que nos aparecer´a, m´ultiples opciones para calibrar la rapidez a la que se mueve nuestro modulo. En la primera parte nos aparece las opciones de rapidez sin pausa, por lo que al dar click en cualquiera de estas opciones sin pausa el veh´ıculo se mover´a durante 5 segundos a lo que debemos medir la distancia que se desplazo el veh´ıculo, esto lo debemos hacer con cada una de las opciones y de esta manera saber cual es la rapidez a la que se mueve nuestro veh´ıculo. Acto seguido nos aparece las opciones de rapidez con pausa, en esta parte el veh´ıculo se mover´a pausadamente 20 veces, por lo que debemos medir la distancia final del veh´ıculo y dividir esta distancia por el numero de veces que se movi´o, de esta manera conseguimos el desplazamiento en cada pausa.

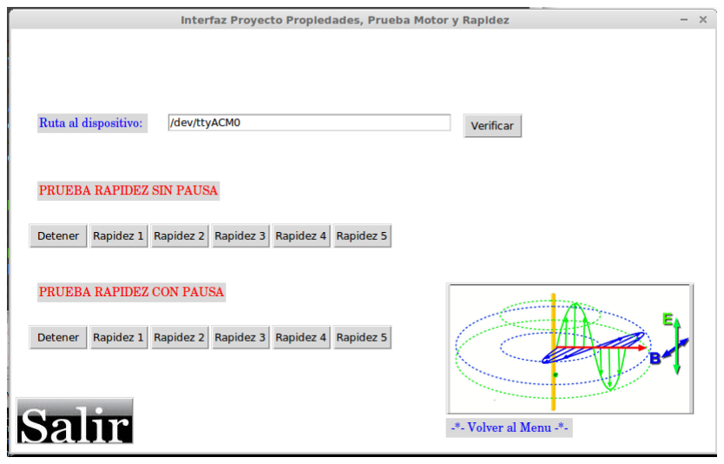
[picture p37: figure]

Figure 10: Este es el programa para realizar las pruebas de rapidez con y sin pausa.

### 3.2 Pruebas sensor lateral

Una vez terminada la prueba de rapidez en el veh´ıculo, damos click en la imagen de una onda electromagn´etica, luego oprimimos en el bot´on que dice prueba 2, una vez all´ı volvemos a colocar la ruta a nuestro dispositivo, que es la misma que la prueba 1; damos click y nos aparecen dos pruebas una con rapidez sin pausa y otra de rapidez con pausa; el principio que utilizamos aqu´ı es el de electro-recepci´on pasiva[8], pues nuestro diodo receptor[5] solo esta recibiendo la radiaci´on y este a su vez se comporta como un transductor[8], pues convierte nuestra radiaci´on electromagn´etica²² o los fotones²³, en electricidad, que es interpretada por nuestro microcontrolador como aumento en la corriente en uno de sus pines receptores an´alogos, causando una diferencia de potencial[8], con esta diferencia de potencial se trabajara para calibrar nuestro instrumento y poder hacer de el lo m´as confiable que se pueda en cuanto a sus mediciones refiere.

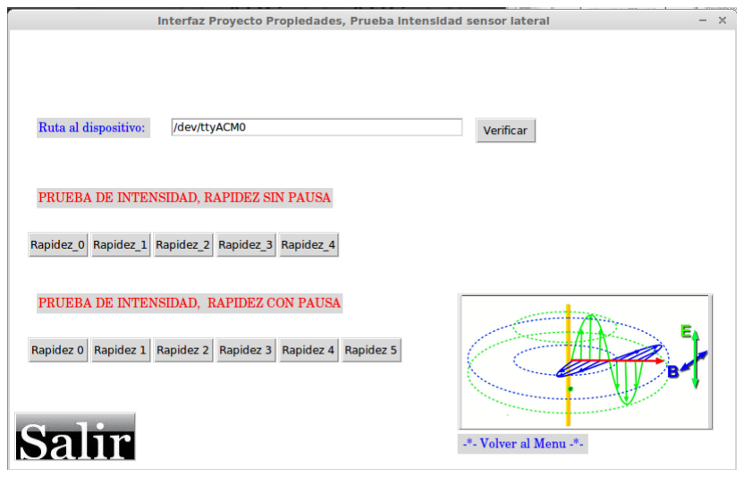
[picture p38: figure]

Figure 11: Este es el programa para realizar las pruebas del sensor lateral.

Para realizar la prueba de rapidez sin pausa es necesario un ambiente²⁴ controlado,²⁵ ahora lo primero sera medir la cantidad de datos que es capaz de procesar nuestro ordenador por segundo, para esto oprimimos el bot´on de rapidez 0 y cambiamos a la ventana de la terminal que esta

21Ver figura 10.
22Parte cl´asica.
23Parte cu´antica.
24No debe estar presente la luz solar ni ninguna fuente que genere cantidades significativas de radiaci´on infrarroja. 25Una temperatura ambiente inferior a los 18 C⁰
, las hojas de datos de estas piezas electr´onicas indican que a temperaturas superiores la corriente no es lineal.
26Para mayor informaci´on de esta parte, favor oprimir el bot´on de ayuda del programa.

ejecutando el programa, una vez all´ı el programa empezara hacer una medici´on del tiempo que tarda nuestro ordenador en procesar 200 datos²⁶, este resultado aparece en nuestra terminal²⁷, mientras captura los datos los gr´afica en tiempo real²⁸; una vez hecho esto cerramos la gr´afica y cambiamos algunas partes del c´odigo²⁹ para medir nuevamente la distancia a la que se desplaza nuestro veh´ıculo despu´es de un tiempo prudencial y de esta manera obtener la rapidez a la que se desplaza nuestro modulo, ahora es necesario volver a cambiar nuestro c´odigo³⁰, esto con el fin de obtener unos buenos datos, por ultimo el programa nos mostrara la cantidad de ruido que interfiere en el experimento.

Ahora hacemos lo mismo con la parte de rapidez con pausa³¹

### 3.3 Pruebas dispositivo frontal

Una vez terminada la prueba 2, damos click en la imagen de una onda electromagn´etica, luego oprimimos en el bot´on que dice prueba 3, una vez all´ı volvemos a colocar la ruta a nuestro dispositivo, que es la misma que la prueba 2; damos click y nos aparecen dos pruebas una con rapidez sin pausa y otra de rapidez con pausa; el principio que utilizamos aqu´ı es el de electro-recepci´on activa[8], este consiste en enviar una se˜nal, y luego por las propiedades[9] de reflexi´on[10], absorci´on[10], atenuaci´on[10], esta llega a nuestro diodo receptor[5], osea que es necesario enviar energ´ıa, para que esta vaya y vuelva rebotando de los obst´aculos a nuestro sensor y este a su vez se comporta como un transductor[8], pues convierte nuestra radiaci´on electromagn´etica³² o los fotones³³, en electricidad, que es interpretada por nuestro microcontrolador como aumento en la corriente en uno de sus pines receptores an´alogos, causando una diferencia de potencial[8], con esta diferencia de potencial se trabajara para calibrar nuestro instrumento y poder hacer de el lo m´as confiable que se pueda en cuanto a sus mediciones refiere.

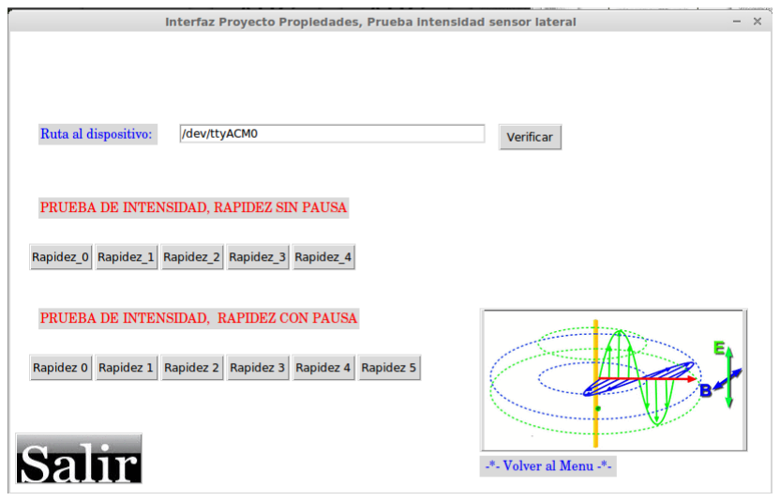
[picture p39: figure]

Figure 12: Este es el programa para realizar las pruebas del sensor lateral.

Para realizar la prueba de rapidez sin pausa es necesario un ambiente³⁴ controlado,³⁵ ahora lo primero sera medir la cantidad de datos que es capaz de procesar nuestro ordenador por segundo, para esto oprimimos el bot´on de rapidez 0 y cambiamos a la ventana de la terminal que esta ejecutando el programa, una vez all´ı el programa empezara hacer una medici´on del tiempo que tarda nuestro ordenador en procesar 200 datos³⁶, este resultado aparece en nuestra terminal³⁷, mientras captura los datos los gr´afica en tiempo real³⁸; una vez hecho esto cerramos la gr´afica y cambiamos algunas partes del c´odigo³⁹ para medir nuevamente la distancia a la que se desplaza nuestro veh´ıculo despu´es de un tiempo prudencial y de esta manera obtener la rapidez a la que se desplaza nuestro modulo, ahora es necesario volver a cambiar nuestro c´odigo⁴⁰, esto con el fin de obtener unos buenos datos, por ultimo el programa nos mostrara la cantidad de ruido que interfiere en el experimento.

Ahora hacemos lo mismo con la parte de rapidez con pausa⁴¹

27El programa va calibrado para trabajar en un ordenador toshiba satellite de 4 Gb de ram.
28Esta parte del c´odigo fue creada por mi al no tener un graficador en tiempo real para el puerto serial en GNU-Linux con python. 29Ver la secci´on ayuda del proyecto.
30Ver secci´on ayuda del proyecto.
31Ver secci´on ayuda del proyecto.
32Parte cl´asica.
33Parte cu´antica.
34No debe estar presente la luz solar ni ninguna fuente que genere cantidades significativas de radiaci´on infrarroja. 35Una temperatura ambiente inferior a los 18 C⁰
, las hojas de datos de estas piezas electr´onicas indican que a temperaturas superiores la corriente no es lineal.
36Para mayor informaci´on de esta parte, favor oprimir el bot´on de ayuda del programa.
37El programa va calibrado para trabajar en un ordenador toshiba satellite de 4 Gb de ram.
38Esta parte del c´odigo fue creada por mi al no tener un graficador en tiempo real para el puerto serial en GNU-Linux con python. 39Ver la secci´on ayuda del proyecto.
40Ver secci´on ayuda del proyecto.
41Ver secci´on ayuda del proyecto.

## 4 Analisis de resultados

### 4.1 An´alisis de la Prueba 1

Despu´es de cerca de 100 mediciones en cada una de las opciones de esa secci´on del proyecto se llegan a las siguientes conclusiones:

### 4.1.1 Rapidez sin pausa

En la tabla 1 se puede apreciar los resultados de la prueba de rapidez sin pausa en cada opci´on del programa, se trabaja con un corriente menor que la salida del pin anal´ogico que es de 35 mA.

El error en la medida de los datos de rapidez es la misma que nos ofrece nuestro instrumento de medici´on que en este caso es un metro cuyo error es +
−

1mm, el error en la medida de la corriente es de +
−

1mA.

Opci´on | m Rapidez ( ) s | Corriente (mA)
Rapidez 1 | 0.103 | 20
Rapidez 2 | 0.130 | 23
Rapidez 3 | 0.138 | 24
Rapidez 4 | 0.154 | 25
Tabla 1. Datos obtenidos de la Prueba 1, rapidez sin pausa, la corrientes es la que circula por el motor con cada opci´on.

### 4.1.2 Rapidez con pausa

En la tabla 2 se puede apreciar los resultados de la prueba de rapidez con pausa en cada opci´on del programa, se trabaja con un corriente menor que la salida del pin anal´ogico que es de 35 mA.

El error en la medida de los datos de rapidez es la misma que nos ofrece nuestro instrumento de medici´on que en este caso es un metro cuyo error es +
−

1mm, no se calcula la
corriente pues varia demasiado rapido para ser medida.
Opci´on | Distancia final (cm) | Avance (cm)
Rapidez 1 | 9 | 0.45
Rapidez 2 | 8 | 0.4
Rapidez 3 | 6.5 | 0.325
Rapidez 4 | 6 | 0.3
Tabla 2. Datos obtenidos de la Prueba 1, rapidez con pausa, la distancia final es la distancia despu´es de 20 repeticiones, y la distancia de avance es la distancia final dividida 20 repeticiones.

### 4.2 Sensor lateral

### 4.2.1 Rapidez sin pausa

En la tabla 1 se puede apreciar los resultados de la prueba de rapidez sin pausa en cada opci´on del programa, se trabaja con un corriente menor que la salida del pin anal´ogico que es de 35 mA.

El error en la medida de los datos de rapidez es la misma que nos ofrece nuestro instrumento de medici´on que en este caso es un metro cuyo error es +
−

1mm, el error en la medida de la corriente es de +
−

1mA.

## References

[1] Arduino, | pagina | oficial, | proyecto | arduino.
http://www.arduino.cc/
[2] Hoja | de | datos | transistor | lm | 7805CV.
http://pdf.datasheetcatalog.net/datasheet/fairchild/LM7805.pdf
[3] Hoja | de | datos | del | transistor | tip | 122.
http://pdf.datasheetcatalog.net/datasheet/fairchild/TIP122.pdf.
[4] Hoja | de | datos | diodo | regulador | 1N4001.
http://pdf.datasheetcatalog.net/datasheet/lrc/1N4001.pdf
[5] Hoja de datos de los diodos led infrarrojos, emisor y receptor.
http://www.datasheetarchive.com/dlmain/Datasheets-31/DSA-617614.pdf
[6] Pagina | oficial | del | proyecto | fritzing
http://fritzing.org/home/
[7] Notas | del | curso, | python | para | el | computo
cient´ıfico, curso de actualizaci´on acad´emica de la DGAPA-UNAM, Facultad de ciencias, Dr. David P. Sanders, 5 de agosto de 2013.
[8] Fundamentos de circuitos el´ectricos, tercera edici´on, editorial Mc Graw Hill, Charles K. Alexander and Matthew N. O. Sadiku.
[9] Berkeley | Physics | Course, | volumen | 3, | Ondas
(Crawford).
[10] Optica, Eugene Hecht, tercera edici´on ´

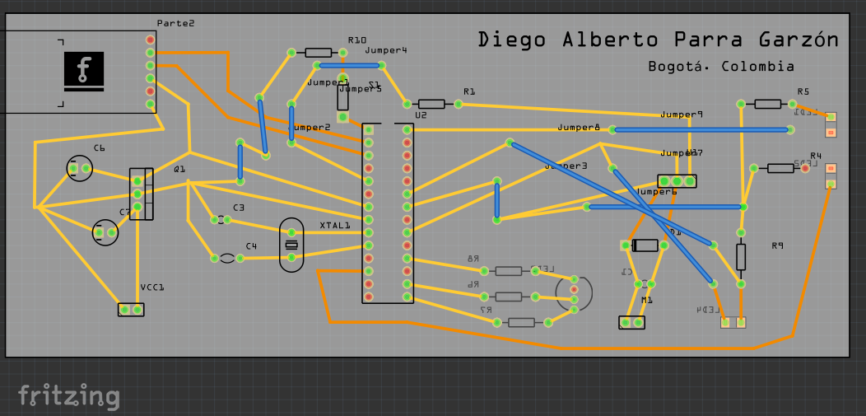
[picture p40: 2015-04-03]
2. Interfaz/2.2 Grafica/prograsecu/Articulos/Montaje Modulo/img/pcb2.png

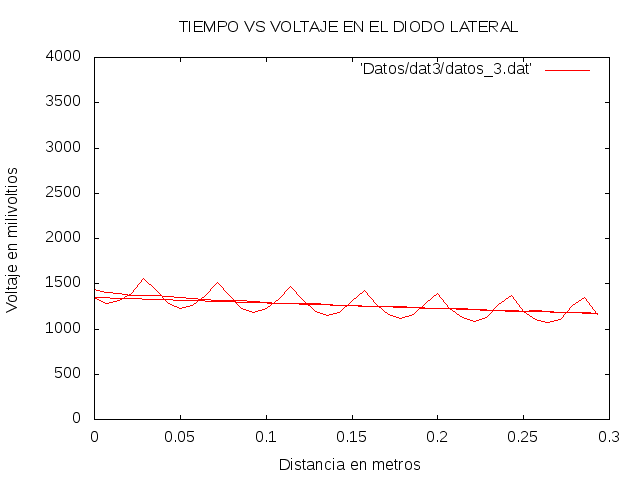
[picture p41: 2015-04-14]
2. Interfaz/2.2 Grafica/prograsecu/Articulos/Montaje Modulo/img/graf13.png

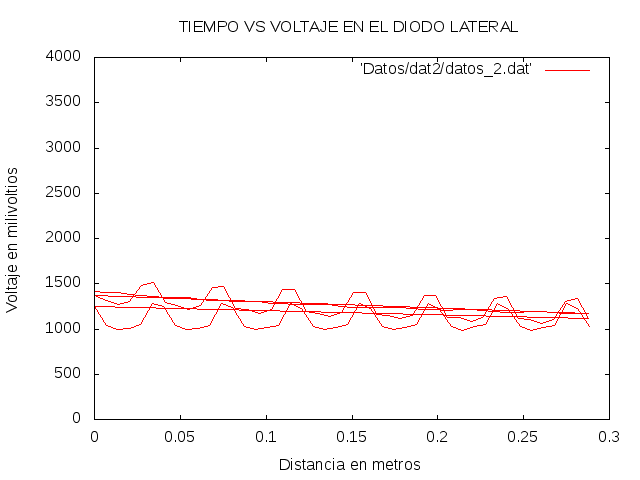
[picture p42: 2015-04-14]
2. Interfaz/2.2 Grafica/prograsecu/Articulos/Montaje Modulo/img/graf12.png

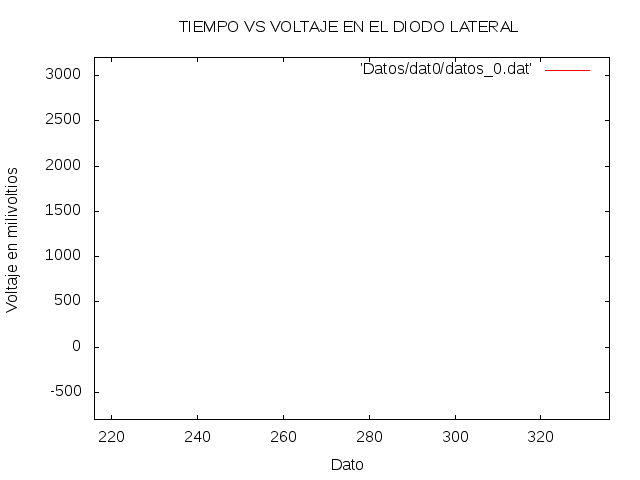
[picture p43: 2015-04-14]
2. Interfaz/2.2 Grafica/prograsecu/Articulos/Montaje Modulo/img/graf10.png

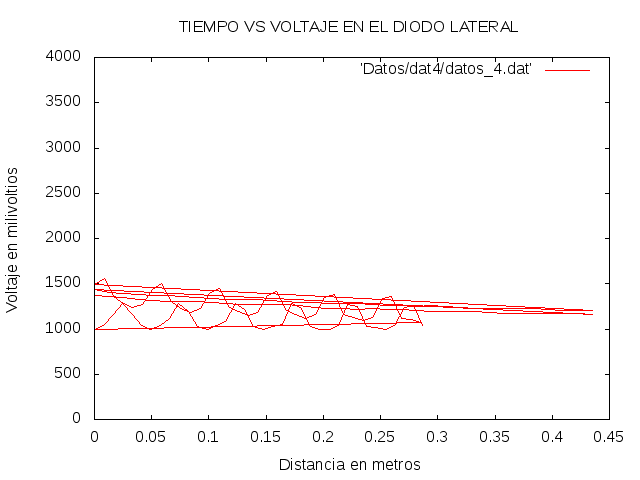
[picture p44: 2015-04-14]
2. Interfaz/2.2 Grafica/prograsecu/Articulos/Montaje Modulo/img/graf14.png

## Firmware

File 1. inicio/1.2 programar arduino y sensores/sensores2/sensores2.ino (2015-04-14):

int motor = 3;
const int sensor1 = A0;
const int sensor2 = A5;
const int ledRojo = 12;
const int ledAzul = 9;
const int ledVerde = 10;
const int ledEmisor = 6;

//variables
long miliVolts1;
long intensidad1;
int brillo1;


void setup()
{
  Serial.begin(9600);
  pinMode(ledAzul, OUTPUT);
  pinMode(ledVerde, OUTPUT);
  pinMode(ledRojo, OUTPUT);
  pinMode(ledEmisor, OUTPUT);
}

void Velo0()
{
      //int  velocidad = map(velocidad,'0', '5', 0, 255);
      //velocidad = 0;
      //analogWrite(motor, velocidad);
      analogWrite(motor, 0);
      delay(20);
}

void Velo1()
{
      //int  velocidad = map(velocidad,'0', '255', 0, 255);
      //velocidad = '150';
      //analogWrite(motor, velocidad);
       analogWrite(motor, 50);
      //delay(20);
}

void Velo2()
{
      //int  velocidad = map(velocidad,'0', '255', 0, 255);
      //velocidad = '160';
      //analogWrite(motor, velocidad);
      analogWrite(motor, 53);
      //delay(20);
}

void Velo3()
{
      //int  velocidad = map(velocidad,'0', '255', 0, 255);
      //velocidad = '170';
      //analogWrite(motor, velocidad);
      analogWrite(motor, 56);
      //delay(20);
}

void Velo4()
{
      //int  velocidad = map(velocidad,'0', '255', 0, 255);
      //velocidad = '180';
      //analogWrite(motor, velocidad);
      analogWrite(motor, 59);
      //delay(20);
}

void Velo5()
{
      //int  velocidad = map(velocidad,'0', '255', 0, 255);
      //velocidad = '190';
      //analogWrite(motor, velocidad);
       analogWrite(motor, 61);
      //delay(20);
}

void Velo6()
{
      //int  velocidad = map(velocidad,'0', '255', 0, 255);
      //velocidad = '200';
      //analogWrite(motor, velocidad);
       analogWrite(motor, 64);
//      delay(20);
}

void Vepa1()
{
  analogWrite(motor, 82);
  delay(55);
  Velo0();
  delay(1000);
}

void Vepa2()
{
  analogWrite(motor, 82);
  delay(50);
  Velo0();
  delay(1000);
}

void Vepa3()
{
  analogWrite(motor, 82);
  delay(45);
  Velo0();
  delay(1000);
}

void Vepa4()
{
  analogWrite(motor, 82);
  delay(40);
  Velo0();
  delay(1000);
}

void Vepa5()
{
  analogWrite(motor, 85);
  delay(48);
  Velo0();
  delay(1000);
}

void Inten1()  
{
  miliVolts1 = (analogRead(sensor1) *5000L) /1023; //opteniendo el valor sensor
  intensidad1 =miliVolts1;
  brillo1 = map(intensidad1, 0, 5000, 0, 255); //funcion map (mapeo) convierte la variable y le da un rango y un dominio
  brillo1 = constrain(brillo1, 0, 255); //funcion constrain o contenido en el intervalo de analogWrite (0, 255)
  analogWrite(ledAzul, brillo1 );   //Salida del led si esta el obstaculo esta lejos
  analogWrite(ledVerde, 255 - brillo1 ); //Salida del led si el obstaculo esta cerca
  Serial.print(" "); //salida al Serialporth
  Serial.print(intensidad1);
  Serial.println(" ");
  delay (60);
}

void Inten2()
{
  miliVolts1 = (analogRead(sensor2) *5000L) /1023; //opteniendo el valor sensor
  intensidad1 =miliVolts1;
  brillo1 = map(intensidad1, 0, 5000, 0, 255); //funcion map (mapeo) convierte la variable y le da un rango y un dominio
  brillo1 = constrain(brillo1, 0, 255); //funcion constrain o contenido en el intervalo de analogWrite (0, 255)
  analogWrite(ledEmisor,   255);
  analogWrite(ledAzul, brillo1 ); //Salida del led si esta el obstaculo esta lejos
  analogWrite(ledVerde, 255 - brillo1 ); //Salida del led si el obstaculo esta cerca
  Serial.print(" "); //salida al Serialport
  Serial.print(intensidad1);
  Serial.println(" ");
  delay (60);
}

void inicio()
{
  digitalWrite(ledRojo, HIGH);   // turn the LED on (HIGH is the voltage level)
  analogWrite(ledAzul, LOW);
  analogWrite(ledVerde, LOW);
  delay(150);               // wait for a second
  digitalWrite(ledRojo, LOW);    // turn the LED off by making the voltage LOW
  analogWrite(ledAzul, LOW);
  analogWrite(ledVerde, LOW);
  delay(150);
}

void Menu()
{
  
  char opcion = Serial.read();
  switch (opcion )
  {
    case 'a': 
            
              
              while(opcion=='a')
              {
                inicio();
                Velo0();
                Menu();              
              }
              break;
              
      case 'b': 
            
              
              while(opcion=='b')
              {
                inicio();
                Velo1();
                Menu();              
              }
              break;
              
      case 'c': 
             while(opcion=='b')
              {
                inicio();
                Velo2();
                Menu();              
              }
              break;
 
     case 'd': 
            while(opcion=='d')
              {
                inicio();
                Velo3();
                Menu();              
              }
              break;
              
      case 'e': 
              while(opcion=='e')
              {
                inicio();
                Velo4();
                Menu();              
              }
              break;
              
      case 'f': 
              while(opcion=='f')
              {
                inicio();
                Velo5();
                Menu();              
              }
              break;
 
      case 'g': 
              while(opcion=='g')
              {
                inicio();
                Velo6();
                Menu();              
              }
              break;
              
      case 'h': 
              while(opcion=='h')
              {
                Velo0();
                Inten1();
                Menu();              
              }
              break;
              
      case 'i': 
              while(opcion=='i')
              {
                Velo1();
                Inten1();
                Menu();              
              }
              break;
 
     case 'j': 
            while(opcion=='j')
              {
                Velo2();
                Inten1();
                Menu();              
              }
              break;
              
      case 'k':
                
              while(opcion=='k')
              {
                Velo3();
                Inten1();
                Menu();             
              }
              break;
              
      case 'l': 
              while(opcion=='l')
              {
                Velo4();
                Inten1();
                Menu();              
              }
              break;
       
       case 'm': 
              while(opcion=='m')
              {
                Velo5();
                Inten1();
                Menu();              
              }
              break;
              
      case 'n': 
              while(opcion=='n')
              {
                Velo6();
                Inten1();
                Menu();              
              }
              break;
 
     case 'z': 
            while(opcion=='z')
              {
                Velo0();
                Inten2();
                Menu();              
              }
              break;
              
      case 'o': 
              while(opcion=='o')
              {
                Velo1();
                Inten2();
                Menu();              
              }
              break;
              
      case 'p': 
              while(opcion=='p')
              {
                Velo2();
                Inten2();
                Menu();              
              }
              break;
 
    case 'q': 
            while(opcion=='q')
              {
                Velo3();
                Inten2();
                Menu();              
              }
              break;
              
      case 'r': 
              while(opcion=='r')
              {
                Velo4();
                Inten2();
                Menu();              
              }
              break;
              
      case 's': 
              while(opcion=='s')
              {
                Velo5();
                Inten2();
                Menu();              
              }
              break; 
              
      case 't': 
              while(opcion=='t')
              {
                Velo6();
                Inten2();
                Menu();              
              }
              break; 
     case '1':
               {
                 Vepa1();
                 Menu();
               }
               break;
  
     case '2':
              {
                Vepa2();
                Menu();
               }
               break;
    case '3':
              {
                Vepa3();
                Menu();
               }
               break;
    case '4':
              {
                Vepa4();
                Menu();
               }
               break;
    case '5':
              {
                Vepa5();
                Menu();
               }
               break;
   }
  
}

void loop()
{
  
  inicio();
  Menu();
    
}

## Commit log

2014-10-26 intrucciones de instalación
2014-10-28 esquema circuito, montaje y placa pcb
    [sensores3.fzz]
2014-10-29 programa para controlar la tarjeta y los sensores
2014-10-29 ordene las carpetas
    [sensores3.fzz]
2014-11-03 cambios en el inicio
2014-11-05 ideo de como abrir una terminal
2014-11-09 Fin del programa de verificación dispositivo
2014-12-21 cambios en la IG
2014-12-23 cambios en imagenes y comienzo del menu
    [sensores3.fz]
2015-01-09 finalizada la prueba 3
2015-03-27 Atenuación
    [tareaf electronica.fzz]
